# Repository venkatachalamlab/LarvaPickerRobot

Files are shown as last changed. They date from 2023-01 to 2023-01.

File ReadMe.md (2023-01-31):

## About

The Larva Picker Robot is an automated system for handling *Drosophila* larvae for continuous long-term observation.
This repository contains the software for driving the robot as well as the analysis tools for the resulting data.

## Table of Contents
1. [Installation](#installation)
2. [Repository structure](#structure)
3. [Getting started](#start)

---

## Installation 

### Dependencies

Make sure that **Python (>=3.6)** and the following packages are installed:
  - dataclasses
  - docopt
  - ffmpeg
  - h5py
  - json5
  - matplotlib
  - numpy
  - opencv-python
  - pandas (==1.4.2)
  - pathlib
  - pyspin
  - scikit-learn
  - scikit-image
  - scipy
  - serial
  - setuptools
  - torch (see [PyTorch.org](https://pytorch.org/get-started/locally/) for instructions on installing with CUDA)
  - tqdm
  - zmq

You may also want the following programs/drivers:
* [SmoothieBoard drivers](http://smoothieware.org/)
* [Pronterface](http://www.pronterface.com/)

### Build from source

1. Clone git repository: 
  ```bash
  git clone https://github.com/venkatachalamlab/LarvaPickerRobot.git
  ```  

2. Navigate to the cloned directory on your local machine.

3. Checkout the current release:
```bash
git checkout v1.0.0
```
Use the following command to see what's new in the most recent release:
```bash
git show v1.0.0
```

4. Install:
  ```bash
  python setup.py install
  ```
  or install in development mode:
  ```bash
  python setup.py develop
  ```

---

## Repository Structure 

**parts** -- contains STL's and SolidWorks files for some of the hardware for the robot as well as a parts list.

**devices** -- drivers for main devices or ZMQ nodes

* `calibrator.py` -- acts as a hub between camera, robot, and the user by taking prompts from CLI to determine if the calibration for the robot needs to be updated, codenamed "lp" for the pub-sub servers
* `camera.py` -- controls camera, codenamed "cam" for the pub-sub servers
* `robot.py` -- controls the Larva Picker robot, codenamed "rbt" for the pub-sub servers
* `larva_picker.py` -- acts a hub between camera and robot by processing the images from the camera to determine when and how the robot should be activated to pick up a larva, codenamed "lp" for the pub-sub servers
* `logger.py` -- handles the video recorder and other writers to save pertinent information to disk, codenamed "log" for the pub-sub servers

**methods** -- functions and variables that are either often used by a device or shared across devices

* `images.py` -- image processing tools
* `loops.py` -- key functions to define different operation protocols used by larva_picker.py
* `robot.py` -- key functions used by robot.py

**config** -- static configuration files

* `constants.py` -- mostly path names for all the key files, some fixed variables like camera resolution here as well
* `\_\_version\_\_.py` -- repository version
* `smoothie_config.py` -- serial configuration for the SmoothieBoard

**utils** -- lower-level code for the robot and templates for ZMQ objects

* `fsSerial.py` -- wraps serial commands to natural language commands
* `robot.py` -- wraps common command sequences to intuitive natural language commands
* `poller.py` -- template for ZMQ poller object
* `publisher.py` -- template for ZMQ publisher object
* `subscriber.py` -- template for ZMQ subscriber object

**analysis_tools** -- tools for data analysis
* **parser** -- image processing tool for detecting, identifying, and separating individual larvae
    * `main.py` -- runs parser
    * `larva.py` -- wraps writers and mutable properties for each individual larva
* **posture_tracker** -- neural network for determining larval posture (outputs head, tail, midspine for each larva in each video frame)
    * `main.py` -- runs posture_tracker
    * `model.py` -- defines layer sequence for the posture_tracker neural network model
    * `flag.py` -- launches UI for producing ground-truth posture data for training posture_tracker
    * `train.py` -- runs training algorithm for posture_tracker
* **state_tracker** -- neural network for classifying larval behavioral state at each time point
    * `main.py` -- runs state_tracker
    * `model.py` -- defines layer sequence for the state_tracker neural network model
    * `flag.py` -- launches UI for producing ground-truth posture data for training state_tracker
    * `train.py` -- runs training algorithm for state_tracker
* **compiler** -- combines results from parser, posture_tracker, and state_tracker across multiple animals to quantify useful behavioral metrics, such as crawl speed, turn rate, thermotaxis index, etc.
    * `main.py` -- runs compiler
* **utils** -- common functions used across analysis_tools
    * `conv_modules.py` -- wrappers for convolution layers, including a convolutional LSTM cell
    * `io.py` -- templates for writers and IO functions
    * `streamers.py` -- PyTorch dataloaders for posture_tracker and state_tracker

---

## Getting Started 

For instructions on how to operate the robot, see [this ReadMe](https://github.com/venkatachalamlab/LarvaPickerRobot/blob/main/larvapicker/ReadMe.md).

For instructions on how to analyze the data taken with the robot, see [this ReadMe](https://github.com/venkatachalamlab/LarvaPickerRobot/blob/main/larvapicker/analysis_tools/ReadMe.md).

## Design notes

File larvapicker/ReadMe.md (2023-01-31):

## About

The Larva Picker is an automated system for handling *Drosophila* larvae for continuous long-term observation.
Follow this ReadMe for instructions on how to operate the robot.

## Table of Contents
1. [Getting started](#start)
2. [Robot calibration](#calibration)
3. [Run larva picker](#run)
4. [Troubleshooting](#troubleshooting)

---

## Getting Started 

Test connection to robot using Pronterface. 
The port the board is using can be checked in the Device Manager and the baudrate is 19,200. Should be able to home robot, then drive in X/Y/Z (positive directions in X/Y to start, negative in Z).

If the robot gives "print paused @__": use command M999. ***ALWAYS RE-HOME ROBOT AFTER THIS COMMAND***
You can also open solenoid valves with M42 and M44 commands (type into Pronterface). M43 / M45 close valves. M105 reads the pressure sensor. 
You can add buttons in Pronterface for those actions. This can be done by using the plus button on the bottom of the grid.

Pressure is controlled by four valves, the air and vacuum valves directly from the source, and the two small valves on robot.
Adjust flow control valves, shooting for a reading of ~50 when vacuum is open, and, ~20 for air.

### Prior to setting up the robot: 
    Pour a large 22cm-by-22cm agar arena.
 
    Make sure that:
    
    The Ethernet cord is connected to the camera
    The Smoothie board is connected to the computer
    The SIM Card is FULLY inserted on the hardware
    The Robot plugged into wall
    The room lights are OFF (It may stay ON during the calibration)
    The LED lights are ON

---

## Calibrating the robot 

      Before continuing:
      
      **Make sure Vacuum is ON, and Air is OFF!**
      Don't be shy about running the calibrations more than once if anything at all goes wrong or seems off!

**1. Make sure Larva Picker software is properly installed onto your environment.**

**2. RUN `camera.py`**

Use the following command:
```bash
camera
```

**3. RUN `robot.py`**

Use the following command:
```bash
robot
```

* Make sure you can see the camera view window and hear the robot booting up.

**3. Check Air and Vacuum pressure**

* When you first boot up `robot.py`, her CLI will prompt you to set up the vacuum and air pressures, respectively. Input "y" or "Y" once the pressure is at a good place (~40 when vacuum is open, and, ~10 for air). Each time you input "n", it will give you the current pressure reading.

* Air and Vacuum can be adjusted in 2 ways:
    * Coarse adjustment from source
    * Fine adjustement from the small knobs attached the the robot
        * Vacuum should be between 30-40, but no more than 52.7
        * Air should be around 10
    
* Wait until you receive the `READY FOR ACTION` message before proceeding.

**4. RUN `calibrator.py`**

Use the following command:
```bash
calibrator
```

**5. Follow the instructions on the CLI for robot calibration.**

* First, the program will ask if you want to update the robot-camera homography, which defines the transformation between the camera or image coordinates to robot internal coordinates.
        * Place a calibration pattern (checkerboard mat works well) on the base plate, making sure the design covers the field of view of the camera
	* Input (type then Enter) yes (or just "y"), the camera will take a picture of the calibration design. The program uses the image to detect corners in the calibration design and mark them on the image.
	* Look at the image that pops up and check that there are enough corners detected (shoot for at least 12 corners), and that there are no false corners (like along the edges of a square) that have been detected as well.
	* If either of these conditions are not met, press "e" in the image window. This will prompt the program to retake the image.
	* If there are issues with the corner detections, it's usually due to dust reflecting light against a black background. You can brush off any obvious particles or wipe it with a wet paper towel. In more extreme cases, you may want to adjust the camera settings like the aperture and exposure.
	* Once satisfied with the corners detected, press "esc" to continue.
	* Now the robot will start and move to each corner that was detected by the camera.
	* At each calibration point, use the WASD keys on the “Robot controller” window to adjust the robot position until it is directly above the corner. 
		* Sometimes the feature detection will slightly be off the corner -- the "Robot controller" window will show you a tiny red dot inside a larger red circle on top of the calibration design for the current calibration point. Try to aim the robot to be directly above the dot. The red circle is approximately the same width as the nozzle tip, so use that to your advantage as well.
		* Press "q" to move onto the next calibration point.
	* Once finished, you will be prompted to save them to the homography file in the *robot’s CLI* (NOT calibrator’s) - input "y" to save.
	* You will be prompted to check calibration. You can reperform the calibration to fine-tune the homography until little to no adjustments are needed during calibration.
	* Remove the calibration design when finished.

#### You should not have to update the homography every single time. If you find that the robot is consistently hitting the correct target during calibration, you can move on. However, the height map DOES need to be recalibrated EVERY time!

* Back on the calibrator’s CLI, the program will ask if you want to update the height calibration.
	* **PLACE THE AGAR ARENA ON THE MOAT PLATE AND FILL THE MOAT WITH WATER BEFORE CONTINUING!** 
	* It's also a good idea to wait a few minutes for the agar to settle and equilibriate with the water. This becomes critical if agar is being reused and was in storage in the fridge prior.
	* Once you input "y", the robot will start and move to each point on the calibration grid automatically and the nozzle moves down towards the agar until it experiences a pressure change when the vaccuuming tip of the probe gets closed off on contact with the agar, leading to no air entering the nozzle. It will read the pressure and record the height at that point and move onto the next calibration point. It will home between each row.
	* Once finished, in *robot’s CLI*, the program will ask if you want to save - input "y" to save.

* The calibrator will take a quick background image for image processing during the experiment and exit out. The camera and robot should still be running.

---  

## Running Larva Picker 

    Prior to picking larva, collect larva from fly vials

**6. RUN `logger.py`**

Use the following command:
```bash
logger
```

* Follow the input prompts to add useful notes for the robot activity log (`log.json`) and metadata (`metadata.json`).

* Otherwise the experiment will not be recorded in any way! Good for testing out hardware or software prototypes, but not if you were planning to use the data.

**7. Set up the experiment arena** 

* Place larvae at the center of the agar bed.

* Fill the water moat with water using the IV system. 
     * You can roll up the roll clamp and run the end around the perimeter of the moatuntil the moat is filled and the water evenly distributed. After the initial fill, you can leave the end on the holder at the top right corner of the moat. You can adjust the roll clamp to provide a steady supply of water, or refill as needed.

**8. RUN `larva_picker.py`** 

Use the following command:
```bash
larva_picker
```

* The program will give you an input prompt for the instar stage. This will influence the size of the larva the process will attempt to detect.

* larva_picker’s CLI will continuously read the images as it is updated by the camera. Check that it is finding the correct number of larvae.

* The correct order of events for picking a larva should be:

	* Identifies larva on perimeter and marks it with a blue rectangle on the image window and alerts you that the robot is being activated with a dramatic CLI alert. [“get_water”]
  	* Moves to closest water moat position and dips into water.
  	* Moves out of the way of the camera if necessary. [“crop_image”]
  	* Refreshes image around the previous larva position (currently a 300x300 box). [“search_cropped_image”]
  	* Attempts to pick up the larva. [“pick_larva”]
	* Moves out of the way of the camera.
	* Refreshes image around the pick up position.
	* If the pick was successful, moves to the middle of the agar and drops off larva. [“drop_larva”]
		* If the pick was unsuccessful, it dips into water and tries again.
	* Moves out of the way of the camera to the left edge. [“search_new_image”]
	* Camera refreshes image around the entire perimeter for any more larva or missed catches.
		* Repeats pick-up/drop-off process if any are detected.
   * If no larva are detected in the perimeter, moves back home and prepares for next larva.
    * Moves back home and prepares for next larva.

* Exit program by pressing "esc" while in the live image feed (The "Image Capture" window). This will cleanly end all processes, including the camera and the robot. [“destroy”]

* Note that there is a video (`movie.mp4`) being written in the dataset folder (which uses the current date), but only while the robot is in STANDBY mode, as well as a timestamped compressed file of the image data (`data.h5`). There is also a log text file (`log.json`) that records detected larva positions during STANDBY and the time stamps for when robot was ACTIVE in units of seconds.
  
---

## Troubleshooting common errors

Every step of these programs can have errors- read this before panicking. 

* If camera fails to open when running `camera.py`:
  * Check to make sure ethernet cord is connected 

* If robot is NOT responding AT ALL:
  * Check to make sure smoothie board is connected, it is plugged into the wall, AND that the sim card on the smoothieboard hardware is fully inserted 

* Troubleshooting connection issues:
  * Device manager is your friend, check to make sure smoothieboard is running correctly on the correct port
  * A “G-drive” should open inside your finder when the smoothieboard is running properly, if this drive is not present it may be an issue

* If Pronterface pauses, is unresponsive, is taking too long:
  * M999 resets the robot and Pronterface- **HOME ROBOT AFTER YOU DO THIS**

* If you receive an error message saying “Pressure read too low, is pump/stopcock open?”:
  * Make sure that vacuum and air pressure is correct by using pronterface
  * Make sure vacuum is on and air is off before calibrating 
  * Retype the command: sometimes this error is because of lag, and needs to be retyped a few times before it works 
  
* If robot is not picking up larva:
	* **ADJUST THE VACUUM PRESSURE WITH THE MANUAL VALVES IF IT IS HAVING A HARD TIME PICKING UP LARVA (NEEDS MORE VACUUM) OR HAVING A HARD TIME EJECTING IT OUT OF THE NOZZLE WITH AIR (NEEDS LESS VACUUM, or MORE AIR PRESSURE)**
  * Determine at which point there is an issue
    * If it does not move to the correct position:
      * The XY coordinates are off and you should recalibrate the homography.
    * If it does not move down far enough to reach the larva:
      * The Z coordinates are wrong and you should recalibrate the height map.
    * If it is not putting the larva down after picking it up:
      * The water is **CRUCIAL** to this- check to make sure moat is appropriately filled, and that nozzle reaches the water correctly 
    * If motor stalls, makes a funny noise, and does not return to home:
      * First see if robot's automatic reset protocol functions normally by pressing "SPACE" on the camera window. Otherwise, robot's process will exit.
      * Relaunch `robot.py` and press "SPACE" on the camera window

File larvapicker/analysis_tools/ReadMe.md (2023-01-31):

## About

The Larva Picker is an automated system for handling *Drosophila* larvae for continuous long-term observation.
Follow this ReadMe for instructions on how to analyze the data obtained with the robot.

## Table of Contents
1. [Tracking larvae](#parser)
2. [Tracking posture](#posture_tracker)
3. [Classifying behavior](#state_tracker)
4. [Compiling behavioral features](#compiler)

---

## Tracking larvae 

**1. Check saved files**

Check that your dataset has been saved with this structure:

```
└── dataset_path
│   ├── data.h5
│   ├── log.json
│   ├── metadata.json
│   └── movie.mp4
```

**2. RUN `parser`**

Use the following command:
```bash
parser --dataset_path=<dataset_path> --n_larva=<n_larva>
```

You can use the movie or log saved with the data to manually check the number of larvae present. There should be at least one frame where the correct number of larvae are visible at once.

The parser will track each individual larva throughout the video and generate a new data file with isolated crops around each larva.

The resulting file structure should look like this:

```
├── dataset_path
│   ├── data.h5
│   ├── log.json
│   ├── metadata.json
│   └── movie.mp4
├── 0
│   ├── data.h5
│   ├── coordinates.h5
│   └── movie.mp4
├── 1
│   ├── data.h5
│   ├── coordinates.h5
│   └── movie.mp4
...
```

---

## Tracking posture 

**3. RUN `posture_tracker`**

Use the following command:
```bash
posture_tracker --dataset_path=<dataset_path> --checkpoint_path=<checkpoint_path> --batch_size=<batch_size>
```

`checkpoint_path` should point to a PyTorch file `checkpoint.pt` that contain the trained model weights for the PostureTracker neural network.

`batch_size` can vary depending on the hardware's memory limits, but ~200 is a good default.

The PostureTracker will analyze each crop to identify the head, tail, and midspine of the larva. 
This information is saved in `pt_results.h5` and will be passed into the StateTracker. 
You can always check the results by reviwing the generated movies, `pt_pred.mp4` (raw probabilities from network) and `pt_results.mp4` (final coordinates for posture points).

---

## Classifying behavior

**4. RUN `state_tracker`**

Use the following command:
```bash
state_tracker --dataset_path=<dataset_path> --checkpoint_path=<checkpoint_path> --batch_size=<batch_size>
```

`checkpoint_path` should point to a PyTorch file `checkpoint.pt` that contain the trained model weights for the StateTracker neural network.

`batch_size` can vary depending on the hardware's memory limits, but ~5000 is a good default.

The StateTracker will analyze the coordinates produced by the parser and PostureTracker to classify each frame into a behavioral state ("RUN" or "TURN"). 
This information is saved in `st_results.h5` and wil be passed into the compiler. 
You can always check the results by reviwing the generated trajectory marked with the corresponding behavior state, `st_results.png`.

---

## Compiling behavioral features

**5. Create an index of datasets to be compiled together.**

> This step is **OPTIONAL** if you are only analyzing a single dataset.

Create a file named `index.json` and populate it as a jsonified dictionary of paths to datasets that will be compiled together into behavioral statistics and features.

**6. RUN `compiler`**

Use the following command:
```bash
compiler (--dataset_path=<dataset_path> | --index_path=<index_path>)
```
> Note that you cannot specify both arguments. 
> Choose `dataset_path` to analyze a single dataset, or specify the path to your `index.json` in `index_path` to compile multiple datasets together.

The compiler will take all results (`coordinates.h5`, `pt_results.h5` and `st_results.h5`) to calculate behavioral quantities for each larva, and compile all the resulting data together to calculate behavioral statistics for the experiment. 
The results for individual larvae will be saved in their respective directories.
The compiled results will be saved in `larvapicker/analysis_tools/compiler/bin`.

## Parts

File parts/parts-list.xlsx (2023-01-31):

Table 1
 | Qty | Source | Part #
Structural
20x20 x 467.5 | 2 | http://us.misumi-ec.com/ | HFSB5-2020-467.5
20x20 x 387 | 2 | http://us.misumi-ec.com/ | HFSB5-2020-387
20x20 x 347 | 2 | http://us.misumi-ec.com/ | HFSB5-2020-347
20x20 x 100 | 4 | http://us.misumi-ec.com/ | HFSB5-2020-100
20x40 x 467.5 | 2 | http://us.misumi-ec.com/ | HFSB5-2040-467.5
20x40 x 632.5 | 1 | http://us.misumi-ec.com/ | HFSB5-2040-632.5
20x40 x 219 | 1 | http://us.misumi-ec.com/ | HFSB5-2040-219
Wide corner bracket | 2 | http://us.misumi-ec.com/ | HBLFSDK5
Narrow corner bracket | 20 | http://us.misumi-ec.com/ | HBLFSSW5
Narrow rounded bracket | 4 | http://us.misumi-ec.com/ | HBLFSNF5
Camera mount | 1 | ProtoLabs.com
Main platform | 1 | Fremont Laser
Motion
X/Y table | 1 | EBay.com
Linear guide | 1 | McMaster.com | 6203K76
Lead screw | 1 | McMaster.com | 6642K13
Lead screw nut | 1 | McMaster.com | 6642K23
Stepper motor, NEMA 8 | 1 | Amazon.com | B00PJYL6BY
Drag chain | 2 | Amazon.com | B00843VYGO
Manipulation
Venturi manifold | 1 | 3D printed
Solenoid | 1 | Sparkfun.com | 11015
Effector bracket | 1 | 3D printed
Venturi plate | 1 | 3D printed
Luer lock fitting | 1 | McMaster.com | 51525K221
Push-to-connect fitting | 1 | McMaster.com | 52065K449
Blunt needle | 1 | McMaster.com
Electronics
Smoothie Board & regulator | 1 | RobotSeed.com
FPC connector | 1 | DigiKey.com
Misc wire & crimp connectors | 1 | On hand
USB cable | 1 | Amazon.com | B00NH11KIK
Micro-switch | 1 | DigiKey.com | D2F-A
Vision
Camera | 1 | FLIR | GS3-U3-23S6M-C
Lens | 1 | BH Photo | Tamron m111fm16-12mp-16mm
Lighting | 1 | 3D printed
Fasteners
M5 x 10 SHCS | 2 | McMaster.com | 91292A124
M5 x 6 SHCS | 2 | McMaster.com | 91292A189
Bumper | 4 | McMaster.com | 93115K881
Shoulder screw | 3 | McMaster.com | 90265A136
Rubber bushing | 1 | McMaster.com | 9311K53
Low profile socket head screw | 1 | McMaster.com | 90666A124
Nuts for extrusion, M5 | 1 | http://us.misumi-ec.com/ | HNKK5-5
Post-assy extrusion nuts, M5 | 1 | http://us.misumi-ec.com/ | PACK-HNTASN5-5

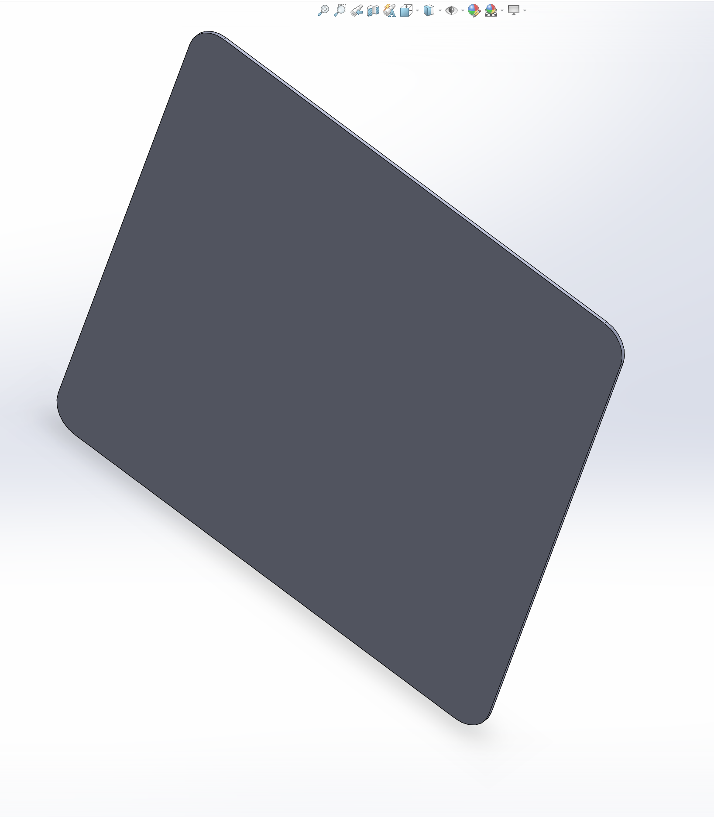
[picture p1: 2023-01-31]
parts/Agar Plates/Agar Plate.PNG

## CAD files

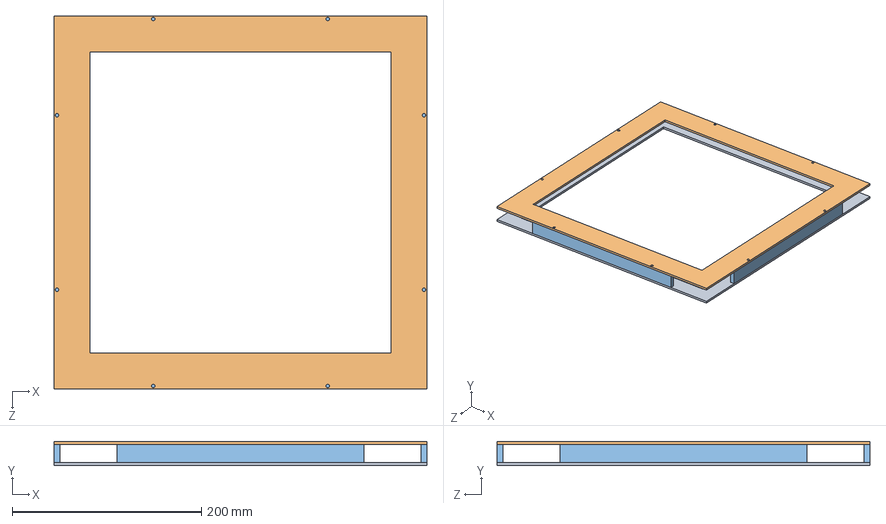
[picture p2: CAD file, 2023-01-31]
parts/LED Frame/Assembly/Assembly.SLDASM
393.7 x 25.4 x 393.7 mm
bottom
top
side x 4

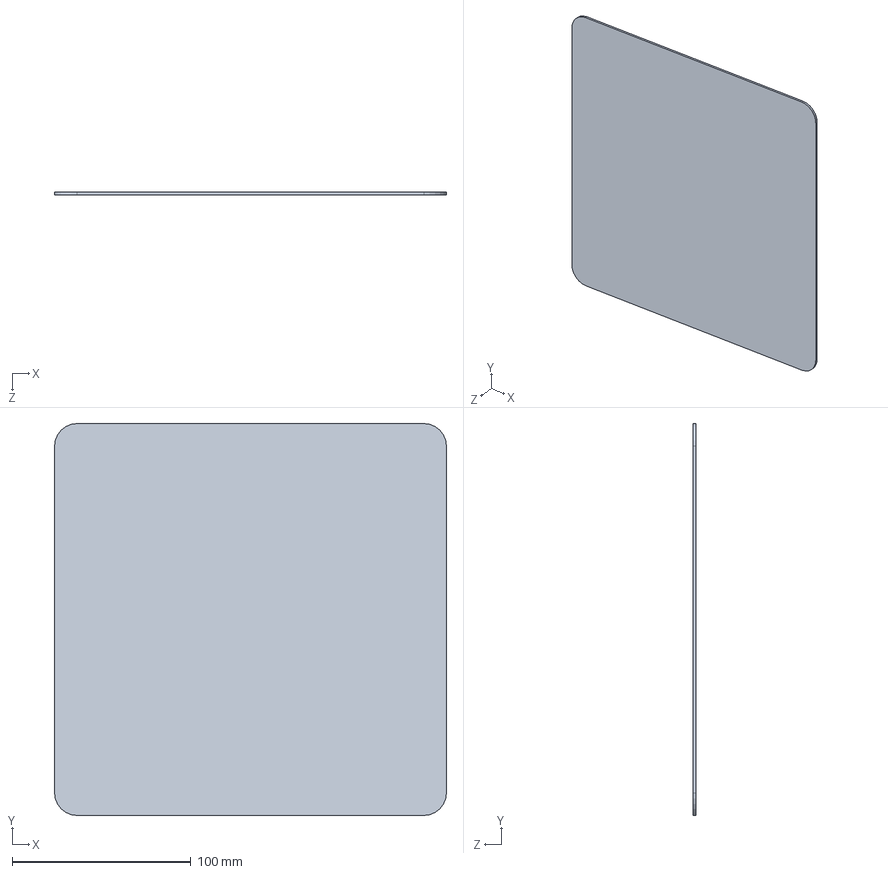
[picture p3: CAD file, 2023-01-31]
parts/Agar Plates/Agar Plate.SLDPRT
219.1 x 219.1 x 1.59 mm

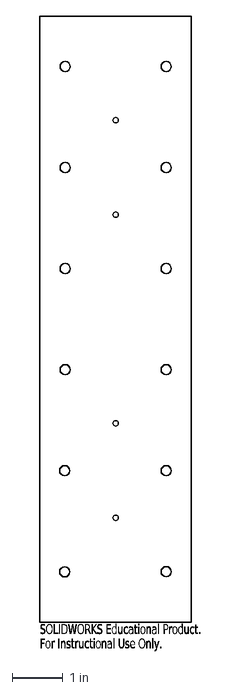
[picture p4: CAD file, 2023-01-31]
parts/Base plate/thermotaxis leg.DXF
SOLIDWORKS Educational Product.
For Instructional Use Only.

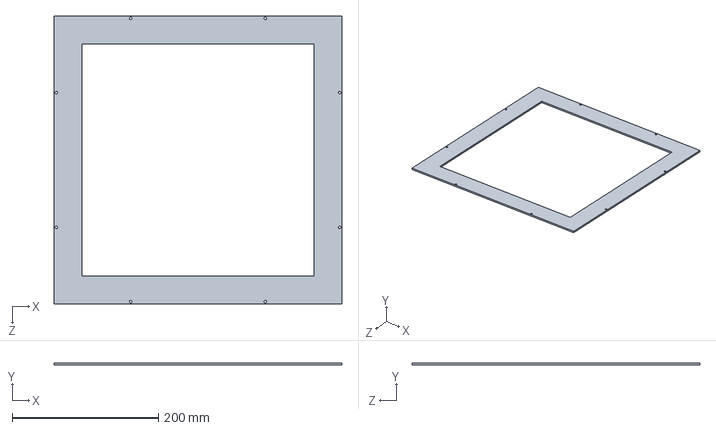
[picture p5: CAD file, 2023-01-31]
parts/LED Frame/SolidWorks/top.SLDPRT
393.7 x 3.17 x 393.7 mm

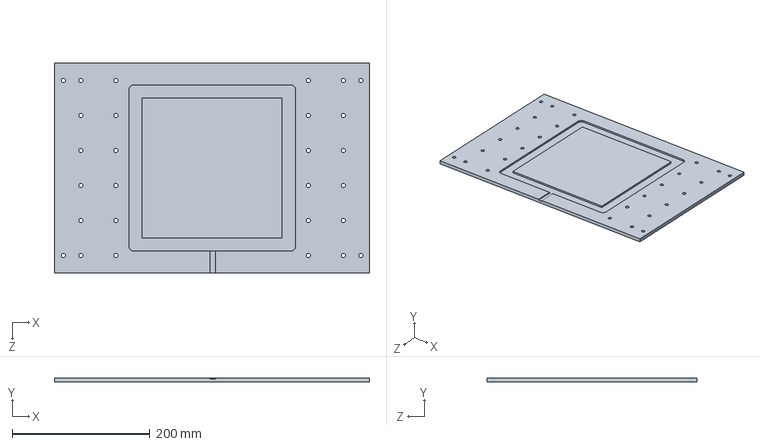
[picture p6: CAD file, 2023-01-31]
parts/Base plate/thermotaxis baseplate.SLDPRT
457.2 x 6.35 x 304.8 mm

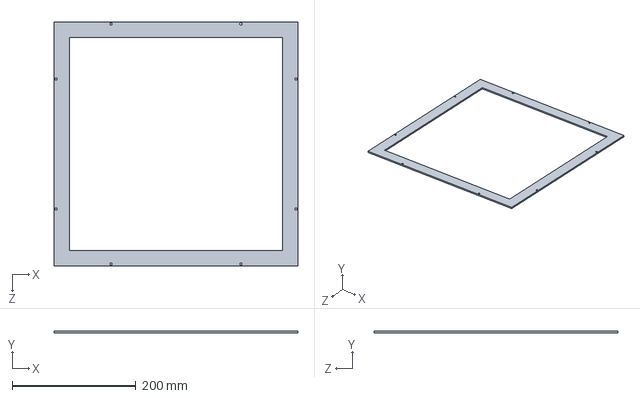
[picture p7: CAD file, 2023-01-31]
parts/LED Frame/SolidWorks/bottom.SLDPRT
393.7 x 3.17 x 393.7 mm

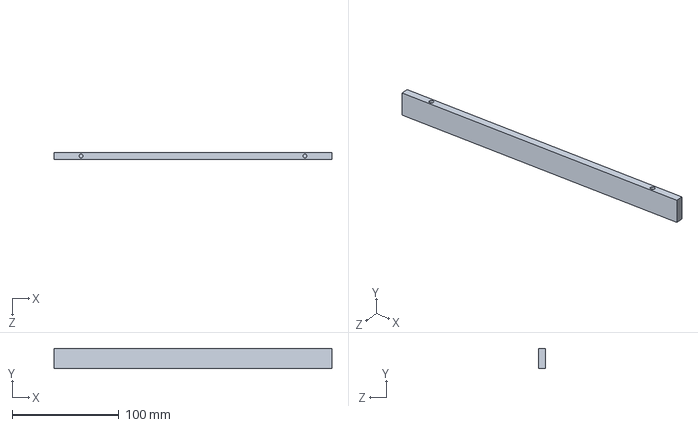
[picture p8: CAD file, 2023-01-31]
parts/LED Frame/SolidWorks/side.SLDPRT
260.3 x 19.1 x 6.35 mm

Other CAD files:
parts/Agar Plates/Agar Plate.SLDDRW
parts/Base plate/thermotaxis baseplate.DXF

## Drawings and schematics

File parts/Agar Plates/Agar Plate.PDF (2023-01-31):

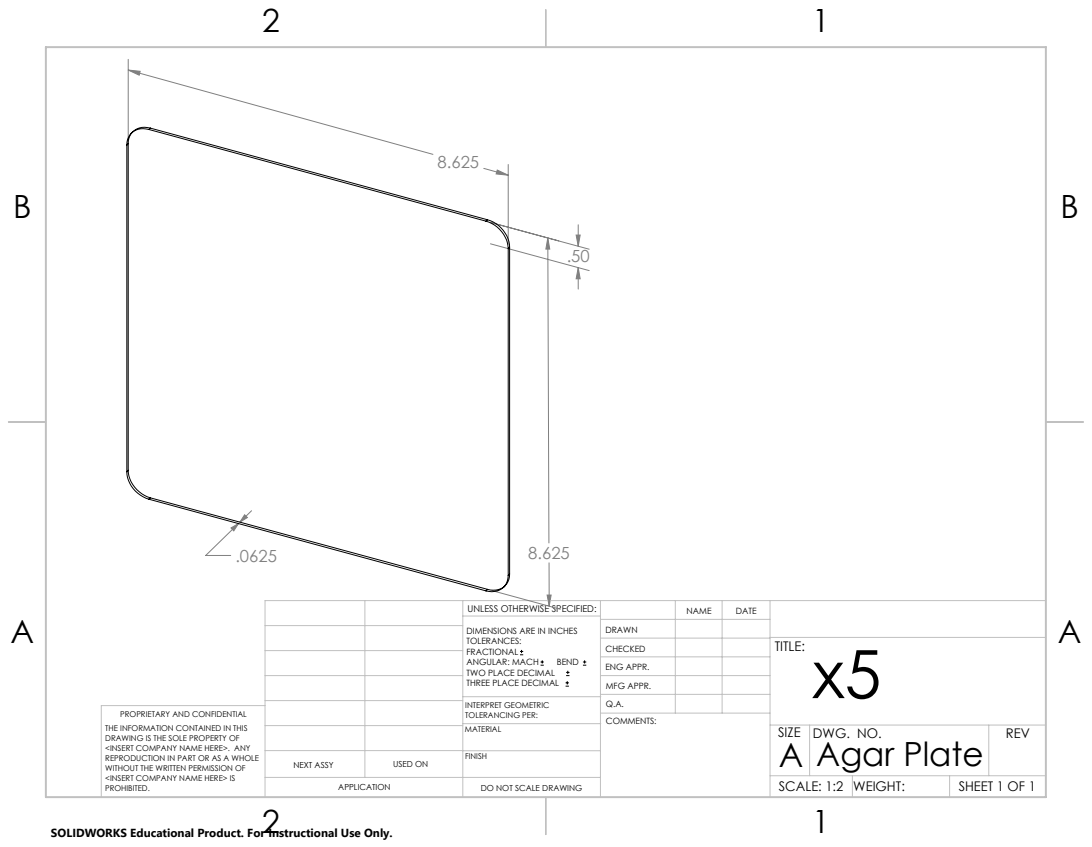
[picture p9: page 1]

UNLESS OTHERWISE SPECIFIED: | | NAME | DATE
DIMENSIONS ARE IN INCHES TOLERANCES: FRACTIONAL ANGULAR: MACH BEND TWO PLACE DECIMAL THREE PLACE DECIMAL | DRAWN
CHECKED | | | x5 TITLE:

ENG APPR.
MFG APPR.

INTERPRET GEOMETRIC TOLERANCING PER: | Q.A.
MATERIAL | | SIZE A | DWG. NO. Agar Plate | REV

PROPRIETARY AND CONFIDENTIAL
THE INFORMATION CONTAINED IN THIS
DRAWING IS THE SOLE PROPERTY OF
<INSERT COMPANY NAME HERE>. ANY
REPRODUCTION IN PART OR AS A WHOLE
WITHOUT THE WRITTEN PERMISSION OF
<INSERT COMPANY NAME HERE> IS
PROHIBITED.

NEXT ASSY | USED ON | FINISH

APPLICATION | DO NOT SCALE DRAWING | | SCALE: 1:2 | WEIGHT: | SHEET 1 OF 1

SOLIDWORKS Educational Product. For Instructional Use Only.

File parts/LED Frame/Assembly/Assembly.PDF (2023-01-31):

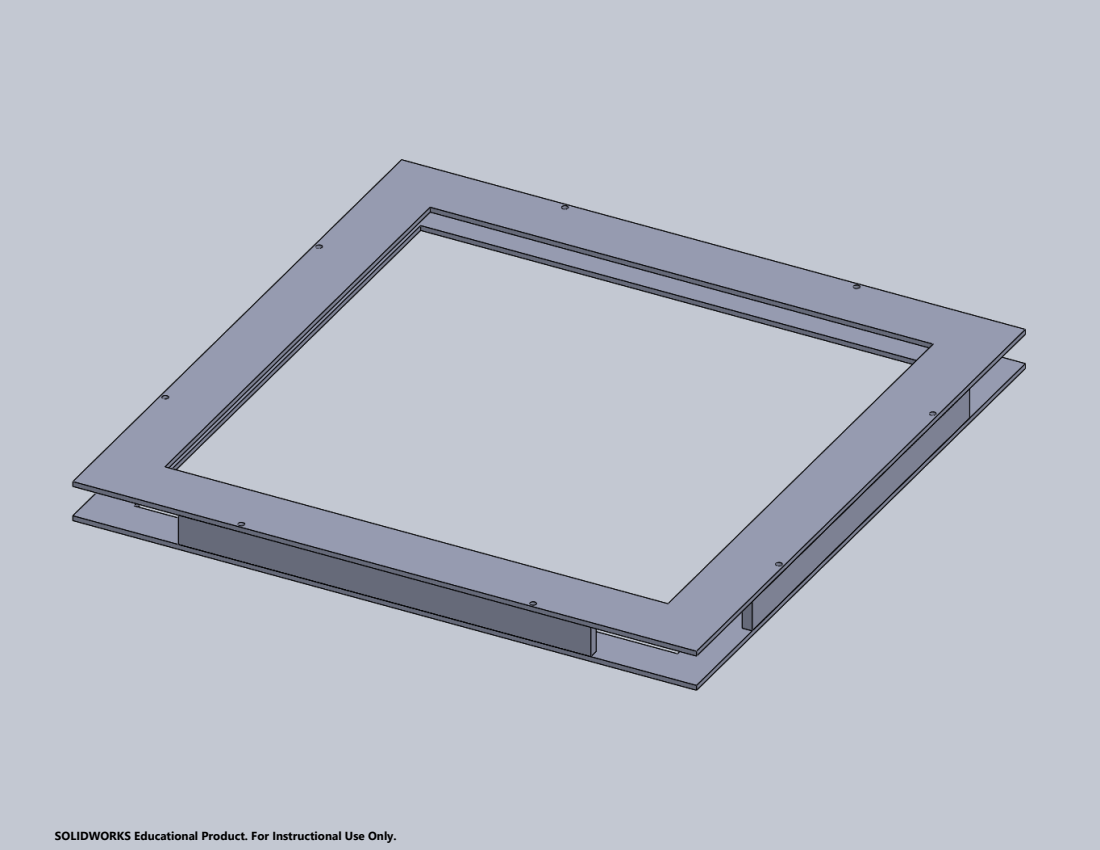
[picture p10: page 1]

SOLIDWORKS Educational Product. For Instructional Use Only.

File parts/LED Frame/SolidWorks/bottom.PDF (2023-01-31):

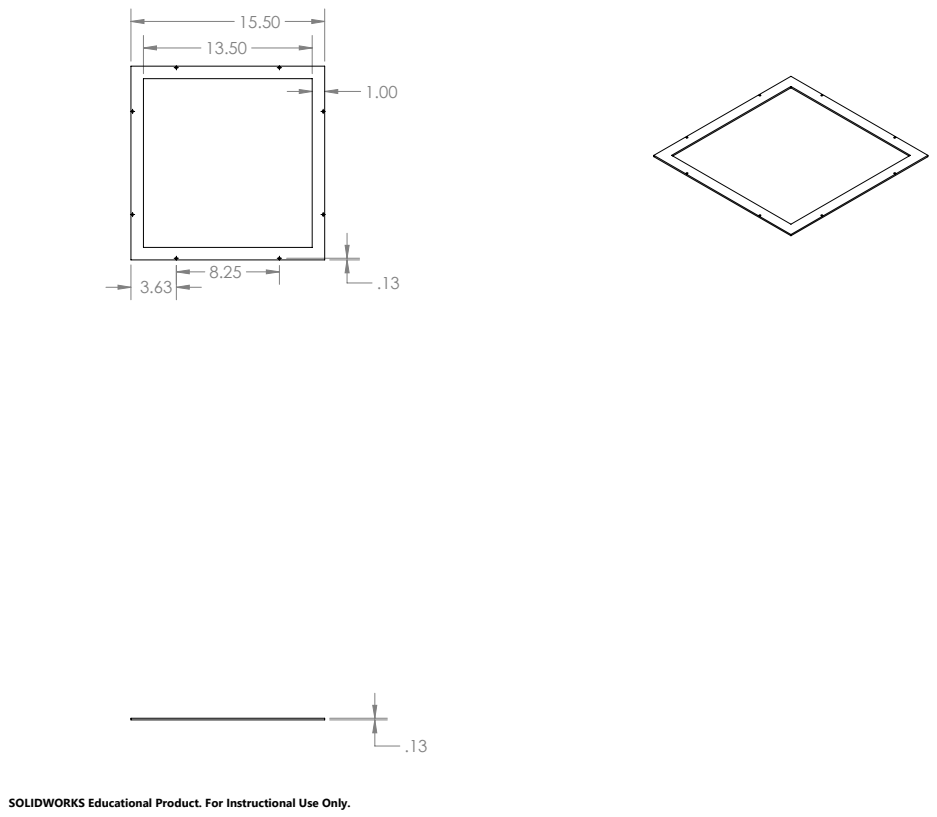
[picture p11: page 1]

SOLIDWORKS Educational Product. For Instructional Use Only.

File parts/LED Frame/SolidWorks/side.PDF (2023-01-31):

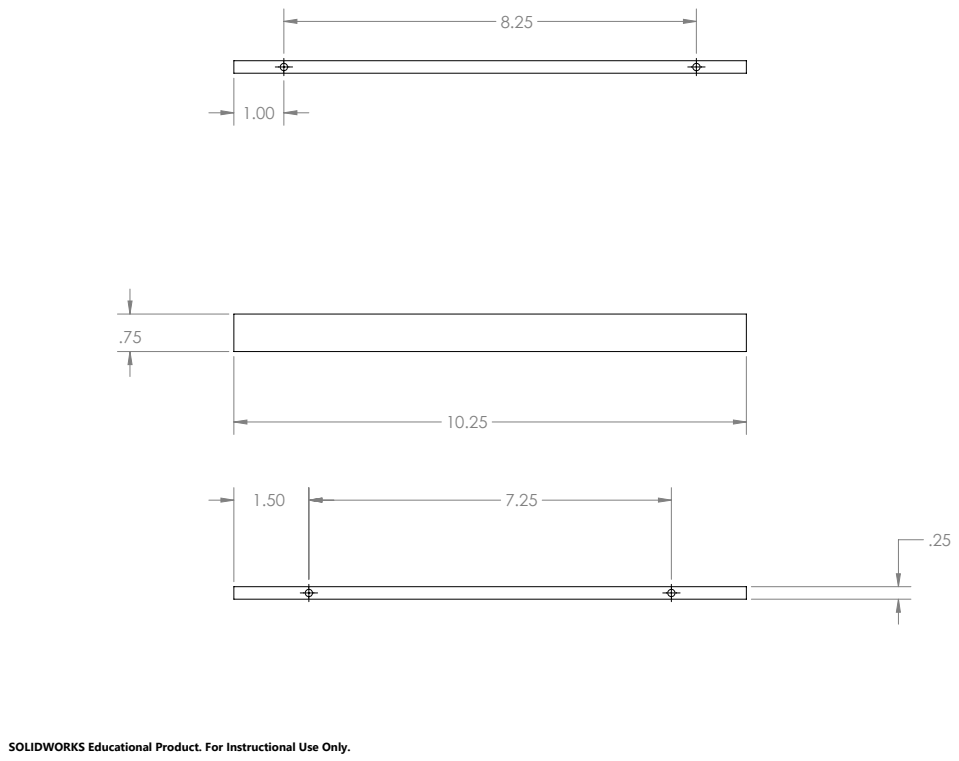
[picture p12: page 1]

SOLIDWORKS Educational Product. For Instructional Use Only.

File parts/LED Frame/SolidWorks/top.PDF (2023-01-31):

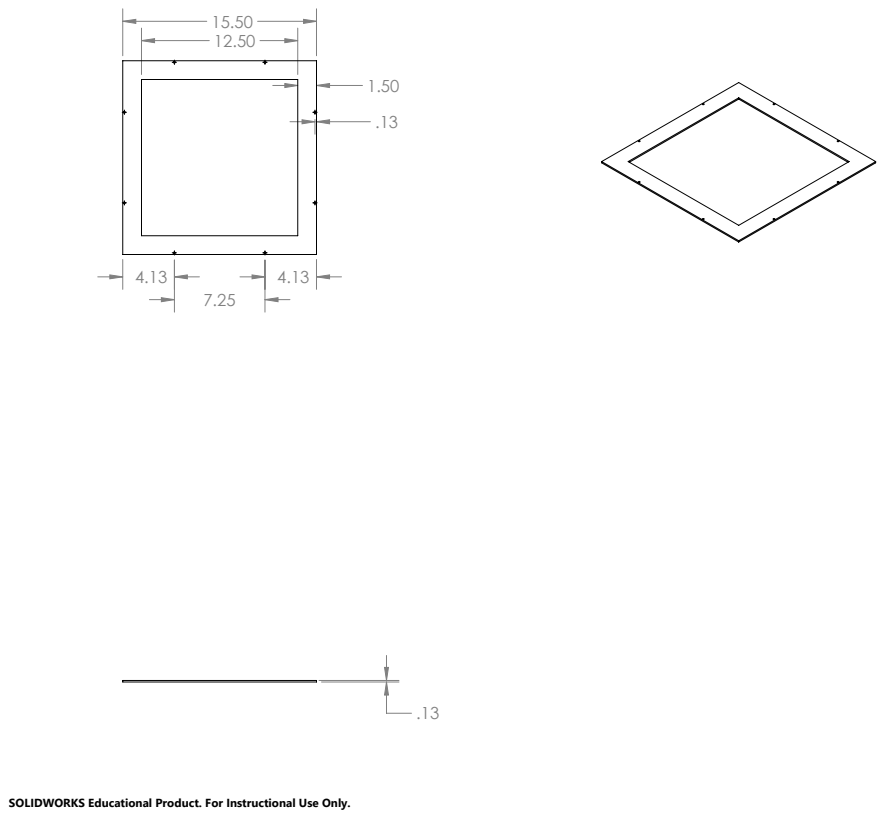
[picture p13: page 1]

SOLIDWORKS Educational Product. For Instructional Use Only.

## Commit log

2023-01-31 Initial commit.
    [Agar Plate.SLDDRW, Agar Plate.SLDPRT, Assembly.SLDASM, bottom.SLDPRT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]
2023-08-23 Update robot.py
    Fixed:
    - robot crashing when initialized without calibration files
2023-09-12 Update robot.py
    - fatal bug when attempting calibration without existing prior calibration file
    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
2024-08-20 Update flag.py
    Fixes:
    - index error with pre-setting head/tail from last frame
